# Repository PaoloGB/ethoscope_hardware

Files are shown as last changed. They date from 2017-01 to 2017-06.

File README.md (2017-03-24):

Ethoscope Hardware
========================
This is the hardware repository of the [ethoscope platform](http://gilestrolab.github.io/ethoscope).
It contains 3d printable files and instructions that altogether should be sufficient to build ethoscopes, arenas and modules.

The software repository lives [here](https://github.com/gilestrolab/ethoscope)

Organisation
==================
This repo is organised as follows:
  1. There is a collection of folders for every part in the Ethoscope.
  2. Inside each folder there is a README file explaining the function of the part and how to put it together.
  3. There is also a folder for each sub-part.
  4. Inside each terminal folder you can find the last version of the hardware with a README explaining its function in detail.

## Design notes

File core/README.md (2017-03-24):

Ethoscope core
==============

This document describes the core of the ethoscope device.
The original onshape repository for the core is available [here](https://cad.onshape.com/documents/56ac957ce4b06a92e0ed7352/w/0af5bcd5aa6f698123921d81/e/9491b49b9158a49e2b29f937).
The "core" referes to device without arena or extra modules.
it is made of three mainparts:

* the **head**, which contains the Raspebbery Pi and its camera.
* the **base**, which diffuses light though different types of arenas (read about arenas [here](../arenas/README.md)).
* the **side walls**, which simply connect the head to the base.

An assembled core looks like this:

finished_ethoscope

Building a core
------------------

A list of all components (or BOM) is available [here](./BOM.csv).

So before we start, we should have something like:

overview

In addition, you will need several tools and consumables such as:

* Allen keys
* soldering iron
* super glue
* heat shrink
* solder wire (lead free).

GPIO connector
----------------

In order to power the infrared (IR) light, the General Purpose Input Output (GPIO) of the  Raspberry Pi is connected to the base by a ribbon cable.
We can build a simple connector that looks like that:

GPIO

Here, we have used a **21cm long** 6 way ribbon cable.

Base
-----------------

The base acts as an IR light box.
The idea is to reflect IR light upward so it can go through the arena.

In order to put the light together, a little bit of basic soldering is required:

IR light soldering

In the figure above, the yellow dashed lined indicate where we need to solder.

You can also notice that **heat shrink** have been put around the wires so that we ensure proper insulation.

After is has been soldered, the led strip must be passed **from the outside** to the inside of the light box by the connector hole.
Then, we can stick the light to its support, and glue the support to the side of the base:

base

Head
--------------------
The head is the single most important part of the device.
It is made of a Raspberry Pi, and peripherals, enclosed by pair(lower and upper) of 3d printed parts.

The steps to build the head are the following:

1. Generate a **SD card**  (it contains the operating system and all the software used by the ethoscope).
2. Plug the SD card in the Pi.
3. Place the **camera** on the lower part, and screw from the outside using M2 bolts along with the nylon nuts (sub-picture A, below).
4. Position the **Raspberry Pi** in the lower part, above the camera, and screw it from the outside, with two M3 bolts (sub-picture B, below).
5. Connect the camera, the **GPIO connector** and the wireless dongle to the Pi.
6. In the upper part, there are four holes in the corners. They allow us to close the box with screws. You want to **insert a nut in each slit** under the hole,
7. Now, we can **close the box** (sub-picture C, below) and screw the upper and lower parts together, using four M3 screws.
8. The last thing we want to do is plugging the micro-usb power supply in the Pi.

Head steps

Last bits:
Before you can start working, you will have to **change the focus of the camera**.
I am afraid this has to be done manually. A very good explanation is available here(TODO).

The wireless dongle blinks with blue light to indicate that it transmits data. 
According to your expoerimental setup, you may want to blind the LED (e.g. with black tape) in order to prevent interference with the behaviour of your experimental animals.

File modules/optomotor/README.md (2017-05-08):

Optomotor Module
=========================

The optomotor is an ethoscope module that allows us to deliver both mechanical (tube rotation) and optical (LED) stimuli to fruit flies held in individual glass tubes.

The original onshape repository for the optomotors lives [here](https://cad.onshape.com/documents/3d4348ea20384ce925691583/w/6966f4288591c2cdd19df81a/e/ab72f28500a5d560744ab72b).

The assembled module will look like this:
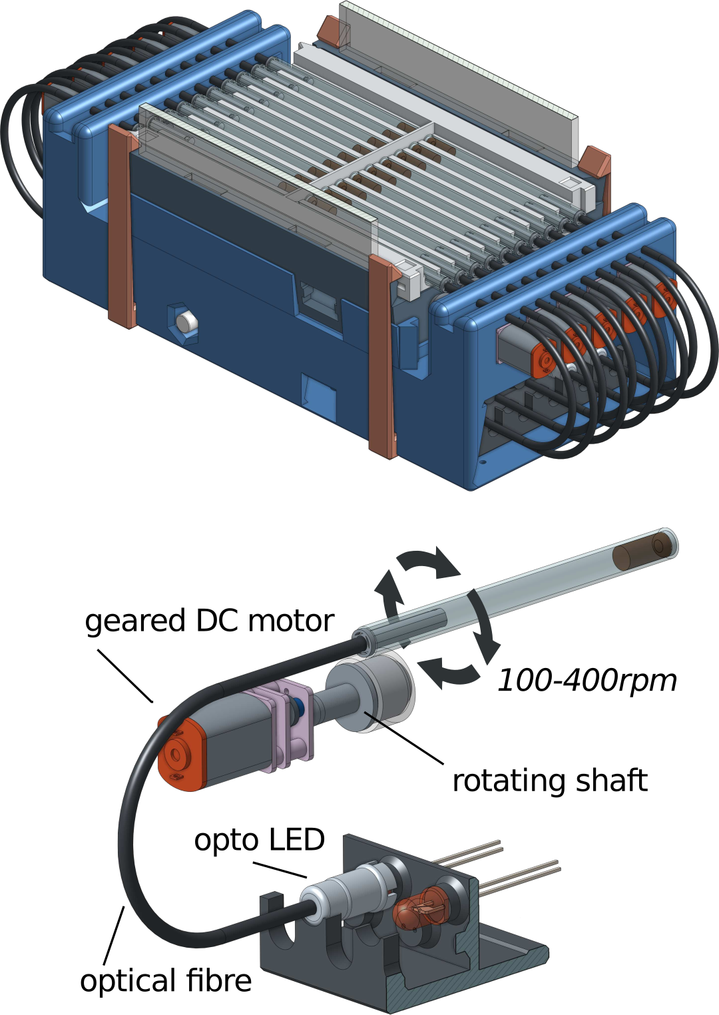
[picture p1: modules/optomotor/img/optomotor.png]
optomotor


Conceptually, the module contains three distinct parts:

* "main", the mandatory components

* "opto", only needed for optical stimulus delivery

* "motor", only needed to rotate tubes

A list of components (BOM) for each part is available [here](BOM.csv).

In this document, we describe how to build both opto and motor parts.

Therefore, before we start, we have something like this:

[[picture overview]]

Main
-----------------------------------------------

The idea is to prepare two electronic boards : [Arduino micro](https://www.arduino.cc/en/Main/ArduinoBoardMicro) and [TLC5943](https://www.adafruit.com/product/1429,15), screw them to the bottom of the main box and connect them to each other.
Also, we add a push button for testing purposes.

###Trimming the main box

The main box is a large print with a lot of support, and it is easier to trim it before putting anything sensitive inside.
Importantly, if you intend to add motors, **ensure you remove all plastic from the cavity that will hold them**.
Indeed, a tiny bit of plastic could end up inside the bear box.

### Arduino board

This is the "master" board that processes input from the computer and coordinate the stimulus delivery.

 1. Solder a 4-pin header (cut a 6-pin header two, 4+2) between pins 3 and 6 (see picture below)

 2. Solder a 2-pin header between pins 11 and 12

 3. Screw the board in place using four 1.2mm diameter screws.

 4. Plug the USB micro cable to the board. Then compile and upload the firmware (you need some degree of familiarity with the Arduino [build process](https://www.arduino.cc/en/Hacking/BuildProcess) for that).
 The code for this firmware lives [here](https://github.com/gilestrolab/ethoscope_hardware/blob/master/modules/optomotor/optomotor.ino).

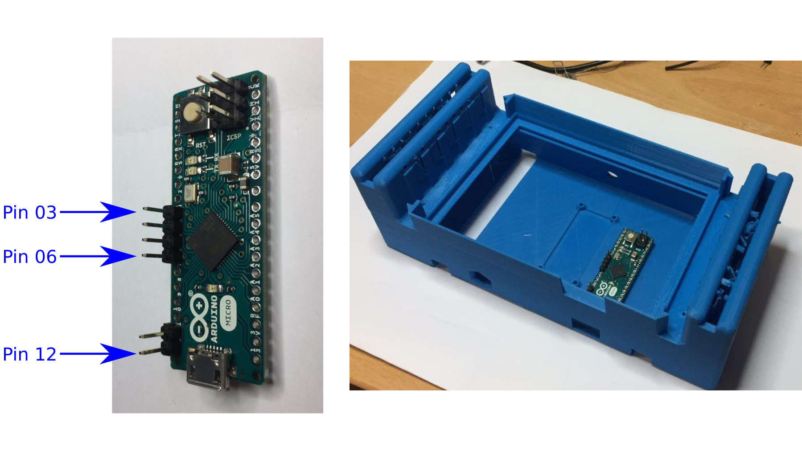
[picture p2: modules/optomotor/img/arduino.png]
arduino


### TLC5943

This board is the "slave".
It is ultimately responsible of turning on/off components (LED/motors).

1. Solder all (i.e. 8) the 6x2 headers (see picture below)

2. Solder the 2 6x1 headers on both extremities of the board

3. Solder the 1.15kΩ resistor

4. Screw the board in place -- using the 2.6mm diameter screws

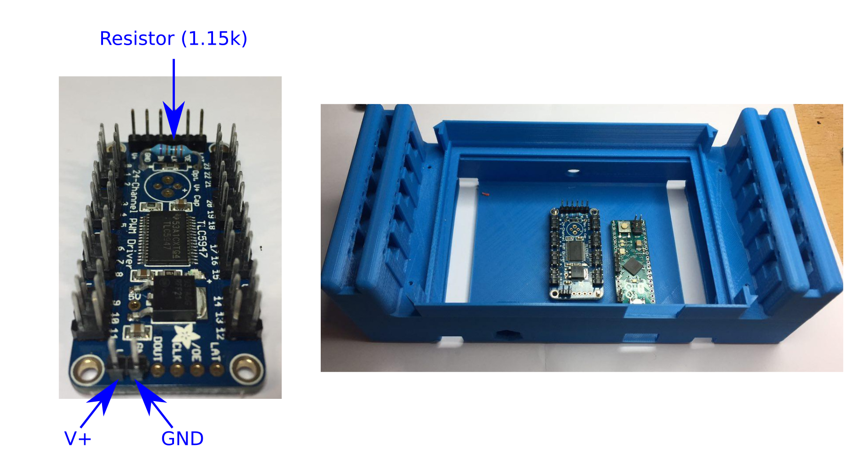
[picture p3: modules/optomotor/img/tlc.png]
tlc


#### Board connector

The connections between the two above boards has to be very robust at all time.

To build the connector (picture below), we use **80mm** of **6-way** ribbon cable. Four of the wires connect the two boards, whilst two bring external power to the TLC5943.

1. Strip all six wires on one end only.

2. Squeeze each wire on a different slot of the 6-way female connector

3. Solder all six wires (this is a bit of a hack, but it works well if you don't have the tool for these connectors)

4. Cut the two wires on the right so that the are only **20mm** long

5. Strip and solder the four remaining wires to the second female connector (the wire must obviously have the same order and position on the second connector -- e.g. in the picture, yellow is on the left of both connectors)

6. Strip the two remaining short wires and add a 2-pin female socket (using two crimps connectors).

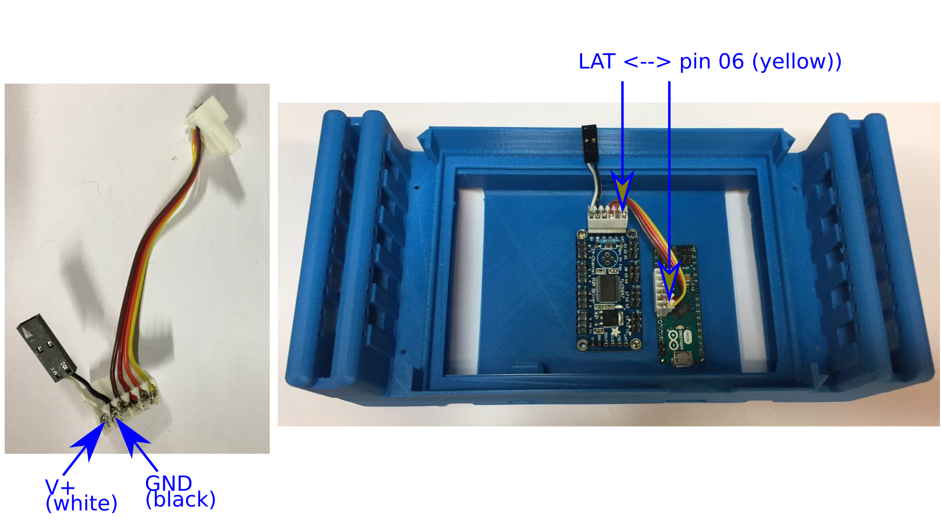
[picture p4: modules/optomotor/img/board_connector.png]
board_connector


###Push button

To assemble the push button:

1. Cut a **150mm**, **3-way** (green, black, white) ribbon cable (picture below)

2. Strip the three wires on one side only, and **preload some heat shrink** before you solder

3. Solder the V+ (white) cable directly to a pin of the push button (it doesn't matter which one)

4. Solder the digital out (green) pin directly to the other pin

5. Solder the ground (black) to the same pin as the digital out, but **through the 1.15kΩ resistor**

6. Retract the heat shrink

7. Cut the ground and V+ wires to **80mm**

8. Use crimps connectors to put ground and V+ in the same 2-pin female socket

9. Use crimps connector to put the digital out wire on a 2-pin female connector (one of the slot will be empty, but do put a crimps connector inside anyway as this makes a better mating between connectors)

10. Bundle all the wires/resistor on the push button end with some larger heat shrink or electrical tape

11. Pass the assembled push button **from the inside of the box to the outside** through the small hexagonal cavity.
Then lock it using the hexagonal screw from the outside.
Admittedly, it is not very easy to spin the push button at this stage, but it will work with some determination!

12. Connect the **V+ and ground pins** to the corresponding pins on the **TLC5943** board

13. Connect the **digital out** wire on **pin 12** of the arduino

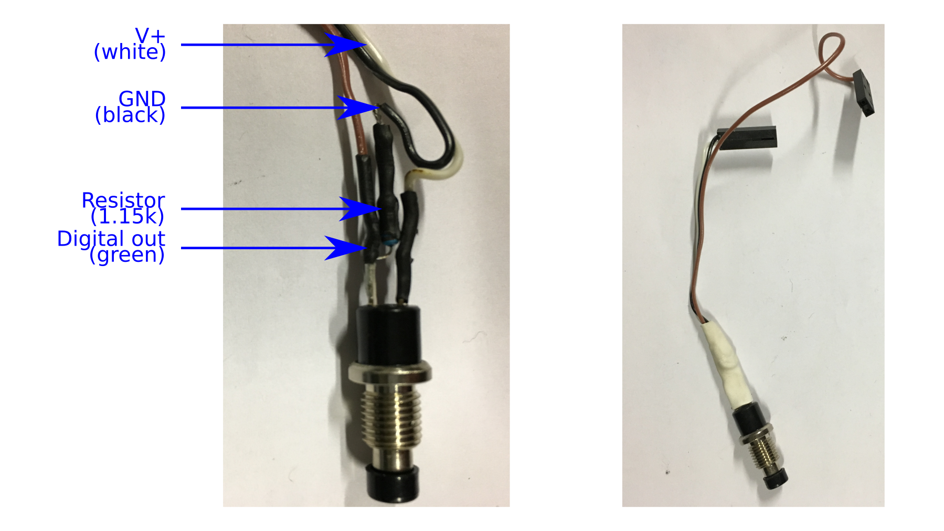
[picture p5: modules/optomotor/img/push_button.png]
push_button


###Power cable

1. Cut the small end of the strip the long USB cable
2. Strip red(V+) and black(GND) cables, cut the others
3. Put some heat shrink around both cables
4. Solder each to a pin of a 2x1 male header
5. Process the heat shrink
6. pass the assembled cable through the circular hole in the back of the box
7. Plug it in the corresponding pins, in the board connector
8. Put a cable tight inside and the outside the box, around the power cable, to prevent stress/disconnection

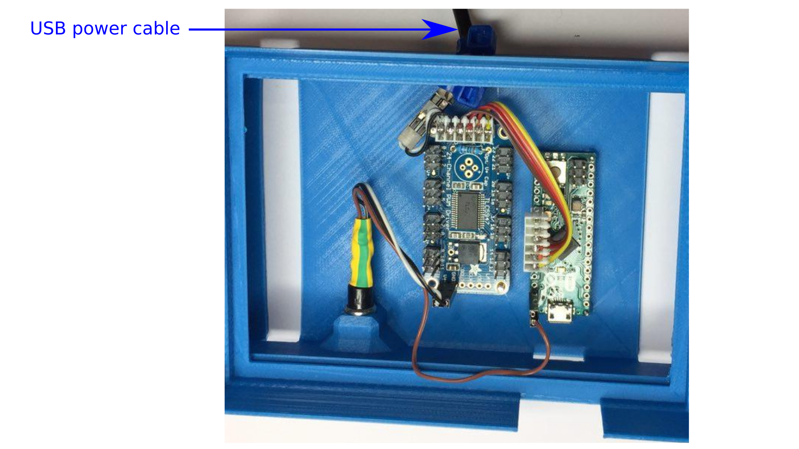
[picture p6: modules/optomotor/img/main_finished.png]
main_finished


Opto
------------------

In order to deliver light to specific tubes, we will make an array of LEDs and connect the LED, with optic fibres, to individual tubes.

Each LED is fitted inside a panel, their are two panels (left and right), each holding five LEDs per machine. The panels are held in position by the "clips"

1. Trim the two panels, so they fit without forcing in the clips.
Also remove any support structure on the LED panels that could have been added by your 3d printer.

2. Set the LEDs so that the **+ side is on the left** (see picture)

3. Cut all the LED legs to 3mm or so

4. Prepare (strip bot ends) as many (10) **75mm**, **2-way** ribbon cables

5. Put a 2-way female socket on one end (using the crimps connectors)

6. Put some heat shrink (5mm should do) on both wires on the other side of the cable.

7. Solder the LEDs. In this document, by **convention**, we use **violet for -** and **light grey for +**

8. Process the heat shrinks

To summarise, this is something like that:

[[picture LED panel]]

Motor
--------------------

Each motor has its own individual slot, so we can just make 10 motors and fit them on the box.
**Ensure you remove all plastic from the motor slots, so that gears don't get stalled**

1. Prepare (strip bot ends) ten **150mm**, **2-way** ribbon cables

2. Put a 2-way female socket on one end (using the crimps connectors)

3. Put some heat shrink (5mm should do) on both wires on the other side of the cable.

4. Solder the motors. In this document, by **convention**, we use **green for -** and **blue for +**.
Each motor will have a small "+" written by the corresponding pole.

5. Pass each motor through its slot in the main box

6. Put its shaft (3d printed small orange part) to each motor

7. Add a ring of silicon (i.e. a section of tube around **5mm long**) to each shaft -- this ensure maximal friction

An assembled motor looks like this:

[[picture assembled motor ]]

Then, when mounted, we have:

[[picture mounted motors]]

Putting things together
-------------------------------------

###Plugging the components to the TLC board.

By convention, **motors are always on even numbers** and **LED, on odd ones**.
In addition, to avoid wires crossing, we map the components the pin facing them, which does not match the numerical order.

So our topology is:

```
MOTOR 01 -> PIN 00  |  PIN 23 <- LED   06
LED   01 -> PIN 01  |  PIN 22 <- MOTOR 06
MOTOR 02 -> PIN 02  |  PIN 21 <- LED   07
LED   02 -> PIN 03  |  PIN 20 <- MOTOR 07
MOTOR 03 -> PIN 04  |  PIN 19 <- LED   08
LED   03 -> PIN 05  |  PIN 18 <- MOTOR 08
MOTOR 04 -> PIN 06  |  PIN 17 <- LED   09
LED   04 -> PIN 07  |  PIN 16 <- MOTOR 09
MOTOR 05 -> PIN 08  |  PIN 17 <- LED   10
LED   05 -> PIN 09  |  PIN 16 <- MOTOR 10
```

## Finishing touches

1. Trim the two clips and fit them on the bottom of the box
2. Lock the clips by sliding the LED panel by the side of the box (if you are not using LEDs, you can simply put panels with no LEDs)
3. Plug both power supply for the TLC and serial connection for the Arduino
4. Press the push button for 5s and release. Check that every component is being activated, in the right order
5. After you have tested the machine, you can decide to mask the various LEDs on both boards if you perform experiments where you don't want any external light
5. Put the roof inside the grove of the box, on top of the boards

[[todo!!]]

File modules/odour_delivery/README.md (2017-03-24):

Odour Delivery Module (ODM) 
=========================
The Odour Delivery Module (ODM) is an Ethoscope module that allows us to delivery up to two different olfactory stimuli to fruit flies held in 14mm glass tubes. 
Odour can be delivered in response to fruitfly behaviour. For instance, following an immobility bout or  a crossing of a virtual midline. 

The ODM can be configured in two different ways; **single** or **dual** odour delivery. 
The frame for dual odour delivery can house two splitters, whereas the frame for single odour delivery houses just one. 
As the former frame is slightly larger, the 3D printed platforms which support the Ethoscope, are slightly different sizes. 
Gcode files for two different versions of the 3D printed frame and platform are available upon request.  
Assembly of the 2 versions of the modules is otherwise similar. 
The assembled odour delivery module with Ethoscope looks like this (this is an example of a a single odour delivery module):

Figure 1 Ethoscope + ODM

A list of components (BOM) for the ODM is available [here](BOM.csv).
In this document we describe how to build the ODM. 
Before we start, this image shows components needed. 
[Pic with all components]
Circuitry
* Cut USB cable 30mm from micro port.  Strip black cable and separate red and black wires inside main cable. Strip black and red cables by approximately 5mm and use micro screwdriver to secure **black cable into VS1-** and the **red into VS1+** on region of lynx motion board labeled 1. 
* Plug in mini port of 2nd USB cable [2].
* Plug in power supply to Anker 40w PSU and USB cable into USB port of computer. **Press the button labeled 3 until green and red lights (labeled 4) are both on and not flashing**. Use a piece of blue tac to cover the lights so they do not disturb the flies during an experiment.
* Place the lynx motion in the base of the frame so that the pins labeled VS1 are in the center.  
* Self-adhesive cable clips can be used to secure the cables and lynx motion into the bottom of the frame (not shown). This can prevent the power supply disconnecting from the lynx motion.

Figure 2 Preparation of Lynx motion
* Next, take the using the 2x10mm screws, secure the 10 x 9G servo motors to the frame of the 2 3D printed shelves (2 screws per servo). 
* Plug the cables of the servo motors into the lynx motion board (Figure 3). The brown cable should correspond to the pin on the outer edge of the VS1 row of pins. The servos should be plugged in the following order:
Servo number
Pin label on lynx motion
1 (shelf 1)
0
2 (shelf 2)
1
3 (shelf 1)
2
4 (shelf 2)
3
5 (shelf 1)
4
6 (shelf 2)
5
7 (shelf 1)
6
8 (shelf 2)
7
9 (shelf 1)
8
10 (shelf 2)
9

* Run script ‘zero_all_servos.py’ to zero all the servos [Q can you update here with link to python script for this part]. 
* Using the 2x6mm screws, screw the cog onto the servos (shortest straight edge of cog should be closest to base of shelf and exactly parallel), whilst they are being locked at 0 position. Make sure that the cogs are tightly secured (these can be printed at 101% to make extremely tight).  
* Insert the Lego Technic Pins. Screw into place using the 2x6mm screws (optional).
 
Figure 3 Servo configuration

Modifying Lego Pneumatic valves
Some of the pneumatic valves are quite stiff and need to be modified; otherwise we find the servos burn out quickly whilst changing lever position during experiments. Please use cut proof gloves and eye protection for this part.
You will need a vice, Stanley knife (with sharp blade), super glue and dust cleaner spray can.
-Place lego pneumatic valve in vice with back edge facing towards you. Using the Stanley knife slice down the grooves between the back panel and valve case. Rotate the valve in vice and cut along the grooves until the glue sticking 3 edges of the back panel to the valve case, is broken.
[Insert pic]
-The back panel is also glued inside the valve to a plastic rod. The dimple in the back of the valve back panel indicates the point of adhesion, so once the back panel is loosened; you will need to slip the knife inside the valve and slice along the back panel to break this glue. To remove the back panel fully you will also need to cut inside parallel to the back panel at two top corners of the valve (see figure?)

[insert pic with cut lines]

- Once the back panel is removed, carefully remove the black lever mechanism. Place somewhere it will not get dusty. It is coated with an oil based lubricant, so be careful not to remove this. 
-Next you will need to remove two small nodules on the inside edge of the valve base. This will allow the black lever mechanism to move more freely from side to side. Do this using the Stanley knife. 
-Clean any shards of plastic from the inside of valve using the dust cleaner spray. Replace the black lever mechanism and stick the back panel back on using a small amount of superglue on each corner. 
-Place in clamp and allow to dry.
-Test valve is working properly and the lever moves freely following this modification. 
Final Steps of Assembly
-Place the 3D printed lever onto the black lever mechanism of the valve (rounded edge down).
- With correct alignment, the two holes in the base of the lego valve should slide onto the lego technic pins (already screwed onto shelves), and the 3D printed lever should slide into the square hole on the 3D printed cog attached to the servo. The lego pneumatic valve should click into place as there is a small lip on the edge of the lego technic pins.
- Next take 1 or 2 fish tank splitters (depending on frame being used) and using a Stanley knife, shorten the length of the input by 15mm. Attach the 10mm OD silicone tubing to the input. Place the 10 or 20 (depending on configuration) 5mmOD12mm lengths of silicone tubing on each of the splitters output. 
[image]
-Thread the 10mm OD silicone tubing through the hole(s) in the 3D printed frame (from inside to out) and slot the fish tank splitter(s) into the groove(s) in the frame. 
-Using the 2x10mm screws, screw the shelves onto the frame,(lego valves facing outwards and servo backs inside). Use sandwich bag wires to tie the servo cables and tuck under the shelves. 
* make sure that servo 1 is to the front left hand side of the ODM Servo 10 should be back right hand corner  (when the hole(s) for the 10mmOD tubing is facing you).
- For single odour delivery, attach the 5mmOD silicone tubing (which is attached to splitter to the lower port of each valve (Figure 4).

Figure 4 Single odour delivery
-For dual odour delivery, attach all 5mmOD silicone tubing originating from one splitter to the upper left port and all of the 5mmOD silicone tubing originating from the second to the upper right port (Figure 5). 

Figure 5 Dual odour delivery
- Using 2x6mm screws attach 3D printed platform to top of frame. There are two Gcode versions of this platform depending on whether you are using frame designed to hold 1 or 2 fish tank splitters (Figure 6). The Ethoscope sits on top of the ODM. Flies within the glass tubing (L,OD,ID: 140mm, 5mm, 3mm) in the Ethoscope arena are connected to the odour supply via 5mm (OD) silicone tubing connecting to the left upper port (for single odour delivery) and the bottom middle port (for dual odour delivery). The USB cable from ODM connects to Ethoscope USB port. Both Ethoscope and ODM connect to power supply. 

Figure 6 ODM with platform

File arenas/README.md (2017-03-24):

Arenas
==================

Arenas are a crucial part of experimental design using the ethoscope platform.
The original onshape repository for all arenas lives [here](https://cad.onshape.com/documents/56ac92e6e4b07682577ddeb3/w/f75f54bb0e265153acfec7dd/e/395a5571e38d50273e8a240c).

An arena is physical translation of an experimental paradigm.

With the ethoscope platform, it is possible to work with multiple arenas according to your biological question and model organism.

Arenas are generally 3d printed and can be derived from templates.
Template arena have the suffix **"template"**

There are several conventional sizes of arena that corresponds to the camera mode of the ethoscopes.
namely, the sizes:

* standard 
* *mini* (the keyword mini is in the name of these arenas)

The mini arenas have smaller surfaces and are optimises for HD video acquisition.
The standard size is a good compromise between image surface and time resolution allowing users to perform real time tracking

Adding new arenas
--------------------------

When adding new arena. Please, provide:

* A README with a description (and and name, author, number of rois,...)
* An stl file
* A 1min mp4 video of the arena with animals. It can be done with `ffmpeg` (e.g. `ffmpeg -ss 00:01:00 -i input.mp4  -t 00:01:00  -c:v libx264 -preset veryslow -crf 26  arena_xxx_xxx.mp4`)

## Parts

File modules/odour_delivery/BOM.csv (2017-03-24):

Piece | Part | Quantity | Supplier | Reference
Frame- 2 versions available | Main | 1 | 3D printed | Gcode file available on Gglab Onshape
Shelves | Main | 2 | 3D printed | Gcode file available on Gglab Onshape
Cogs | Main | 10 | 3D printed | Gcode file available on Gglab Onshape
Levers | Main | 10 | 3D printed | Gcode file available on Gglab Onshape
Platform- 2 sizes available | Main | 1 | 3D printed | Gcode file available on Gglab Onshape
LEGO Pneumatic Two-way Valve with Pinholes (47223) | Main | 10 | Brickowl | http://www.brickowl.com/catalog/lego-pneumatic-two-way-valve-with-pinholes-47223
LEGO Technic Pin with Lengthwise Friction Ridges and Center Slots (2780 | Main | 20 | Brickowl | http://www.brickowl.com/catalog/lego-technic-pin-with-lengthwise-friction-ridges-and-center-slots-2780
2x6mm screw | Cog screw | 10 | Amazon | http://www.amazon.co.uk/Tapping-Thread-Round-Phillips-Screw/dp/B00GMQDSRI
2x 10mm screw | Servo, shelf and platform screws | 28 | Amazon | http://www.amazon.co.uk/dp/B00MFBTWMO/ref=pe_385721_37986871_TE_item
9G microservos 4.8V | Circuitry | 10 | roboscop | http://www.robotshop.com/uk/9g-micro-servo-motor-4-8v.html
Lynx Motion SSC-32 Servo Controller | Circuitry | 1 | Roboshop | http://robotshop.com/en/lynxmotion-ssc-32-servo-controller.html
USB A to micro cable | Circuitry | 1 | RS | RS 888-8811
USB A to mini cable (30cm) | Circuitry | 1 | Amazon | http://www.amazon.com/30CM-male-plug-leads-Cable/dp/B00MMVLH9I
10 Way Fish Tank Splitters | odour delivery | 1 o 2 depending on setup | Ebay | http://www.ebay.co.uk/itm/281812927693
Sillicone tubing OD, ID, WT (5mm,3mm,1mm) | odour delivery | 20 x 12mm lengths | VWR
Sillicone tubing OD, ID, WT (10mm,6mm,2mm) | odour delivery | 1 or 2 x 300mm (depending on setup) | VWR
Anker 40w PSU | Power supply | 1 | Amazon | ?

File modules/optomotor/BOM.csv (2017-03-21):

Piece | Part | Quantity | Supplier | Reference | Price(approx., in $) | Stock
Main box | main | 1 | Polygonal Tree/Custom made | TODO | 0
Box clips | main | 2 | Polygonal Tree/Custom made | TODO | 0
Shafts | main | 10 | Polygonal Tree/Custom made | TODO | 0
LED Panels | main | 2 | Polygonal Tree/Custom made | TODO | 0
Circuit roof | main | 1 | Polygonal Tree/Custom made | TODO
USB A to micro cable(50cm) | main | 1 | Farnell | http://uk.farnell.com/multicomp/mc001008/usb2-0-a-male-to-micro-usb-b-m/dp/2506103 | 3
USB A (Power supply) | main | 1 | RS | http://uk.rs-online.com/web/p/products/8888811
Screws (M2.6 x 8mm) | main | 2 | RS | http://uk.rs-online.com/web/p/products/6644956/
Screws (M1.2 x 6mm ) | main | 2 | RS | http://uk.rs-online.com/web/p/products/4187218/
Arduino micro | circuitry | 1 | RS | http://uk.rs-online.com/web/p/products/7798864 | 15
TLC5947 PWM Driver | circuitry | 1 | Adafruit | https://www.adafruit.com/product/1429 | 15
Push button | circuitry | 1 | RS | http://uk.rs-online.com/web/p/products/1336502 | 2.5
PCB Headers (2 x 3) | circuitry | 8 | RS | http://uk.rs-online.com/web/p/pcb-headers/2518137 | 0.2
Right angle 6 way socket | circuitry | 3 | RS | http://uk.rs-online.com/web/p/idc-connectors/5437750/ | 0.3
PCB Header (1 x 6) | circuitry | 3 | RS | http://uk.rs-online.com/web/p/pcb-headers/6812994/ | 0.4
Female 2 pins crimps | circuitry | 20 | Farnell | http://uk.farnell.com/multicomp/2226tg/crimp-terminal-24-28awg/dp/1593506 | 0.24
Crimps contact | circuitry | 40 | Farnell | http://uk.farnell.com/multicomp/2226tg/crimp-terminal-24-28awg/dp/1593529 | 0.06
Ribbon cable | circuitry |  | RS |  | 0
Resistor (1.15k) | circuitry | 2 | RS | http://uk.rs-online.com/web/p/through-hole-fixed-resistors/7548691/ | 0.25
N20 gear motor | motor | 10 | ??? | ??? | 4
Silicon tubing 6x9 mm | motor | 1 | VWR |  | 2
Filter Box | opto | 1 | Polygonal Tree/Custom made | TODO | 0
IR filters | opto | 1 | TODO | TODO | ?
Light Guides (8in) | opto | 5 | RS | http://uk.rs-online.com/web/p/led-light-pipes/8905782 | 2.5
LED Fibre Optic Couplers | opto | 10 | Mouser | http://www.mouser.co.uk/ProductDetail/VCC/THR_5_22/ | 0.6
630 nm LEDs | opto | 10 | RS | http://uk.rs-online.com/web/p/visible-leds/9047367 | 0.15

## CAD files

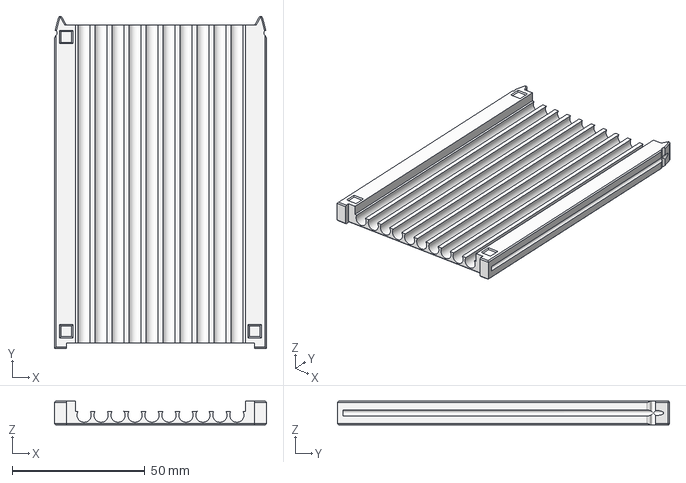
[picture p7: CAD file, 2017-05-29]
arenas/arena_10x1_longTubes/arena_10x1_longTubes.step
80.0 x 125.2 x 9.00 mm

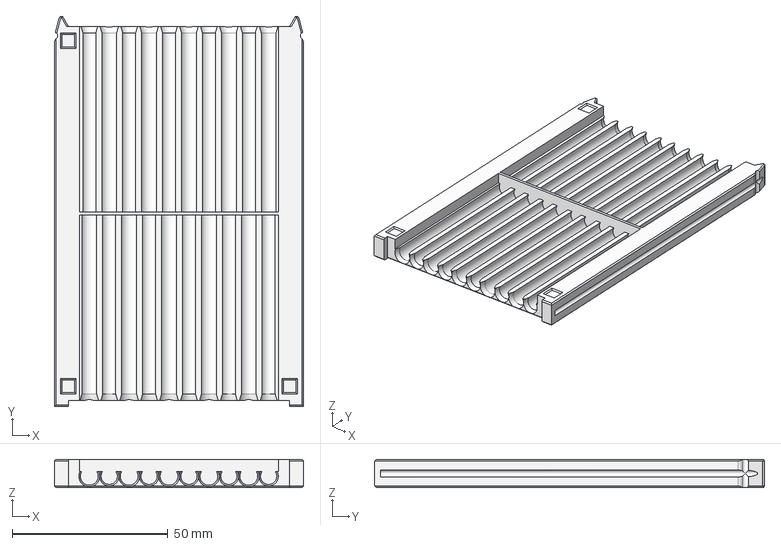
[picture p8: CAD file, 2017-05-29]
arenas/arena_10x2_shortTubes/arena_sdModule.step
80.0 x 125.2 x 9.00 mm

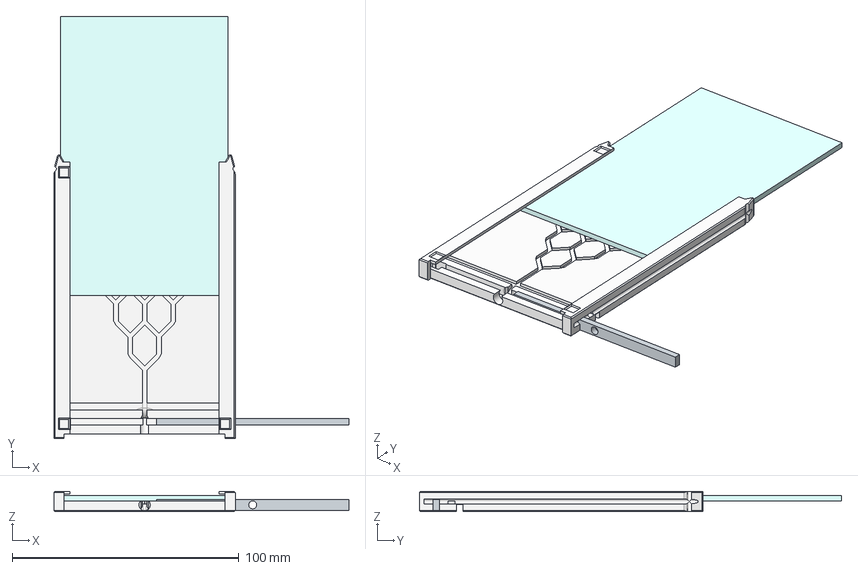
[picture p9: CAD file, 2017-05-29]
arenas/arena_gauss/Gauss.step
130.2 x 186.3 x 9.00 mm
arena_binary_tree
Glass_lid
slider

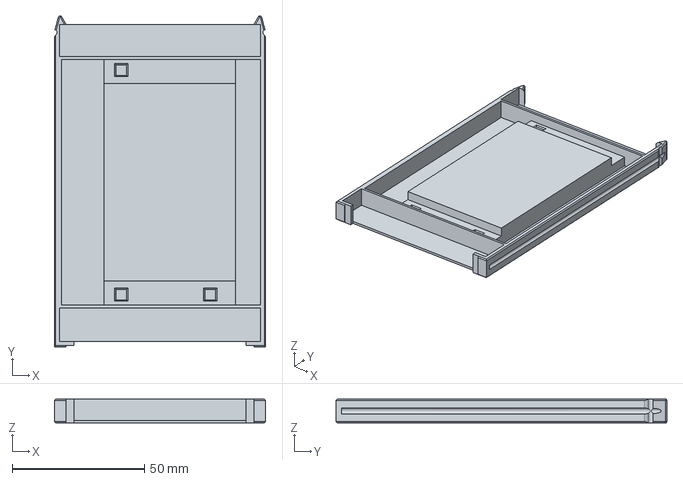
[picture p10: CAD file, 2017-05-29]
arenas/arena_mini_template/arena_mini_template.step
80.0 x 125.2 x 9.00 mm

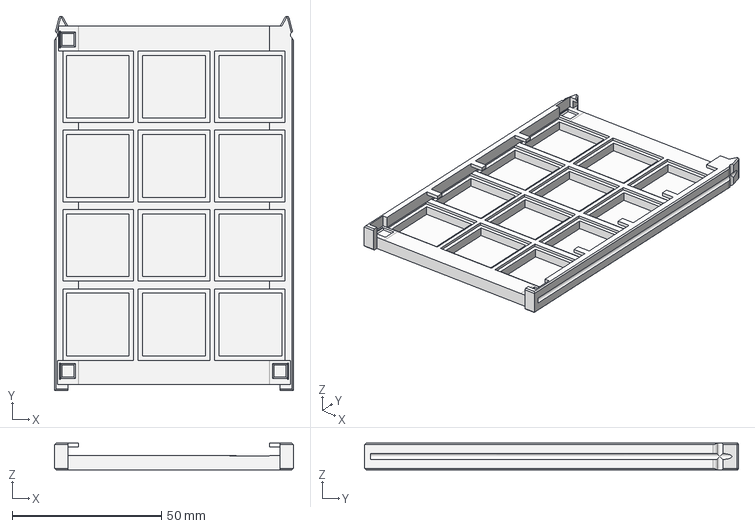
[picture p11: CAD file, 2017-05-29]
arenas/arena_squares/arena_squares.step
80.0 x 125.2 x 9.00 mm

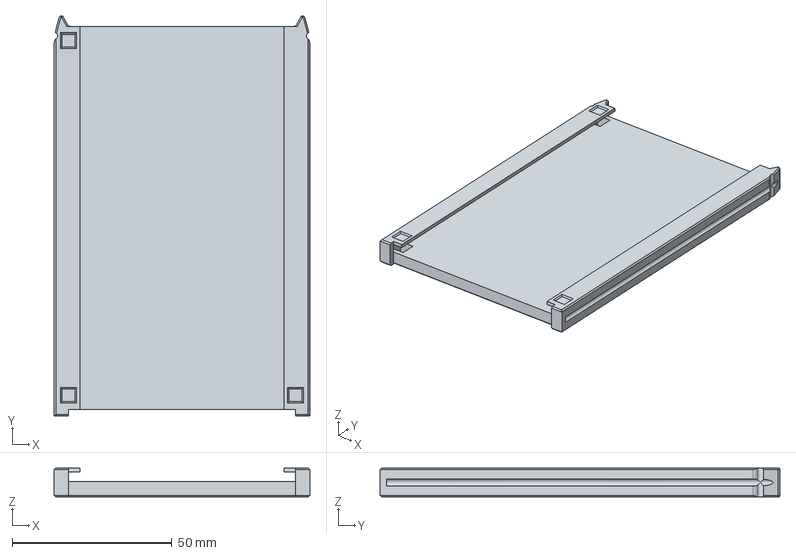
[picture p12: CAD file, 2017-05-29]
arenas/arena_template/arena_glassLid_template.step
80.0 x 125.2 x 9.00 mm

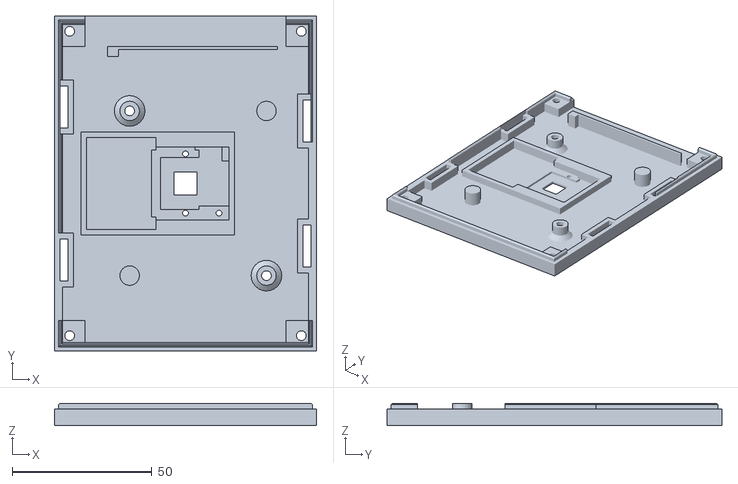
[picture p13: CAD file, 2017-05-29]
core/lower_pi_case/lowerPiCase.stl
94.0 x 120.0 x 8.00

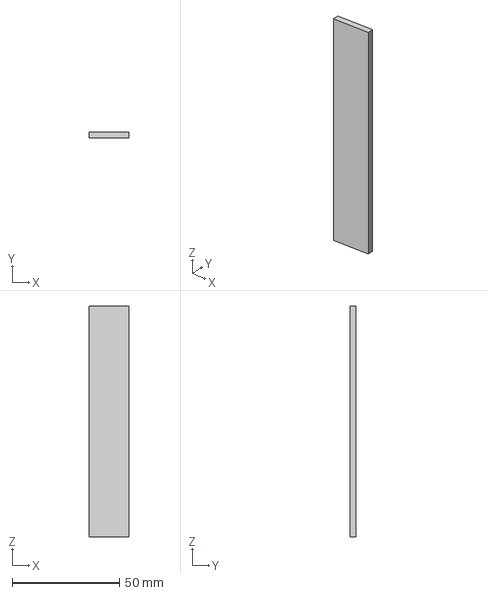
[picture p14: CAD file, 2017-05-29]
core/side_wall/LightTile.step
18.7 x 3.00 x 107.7 mm

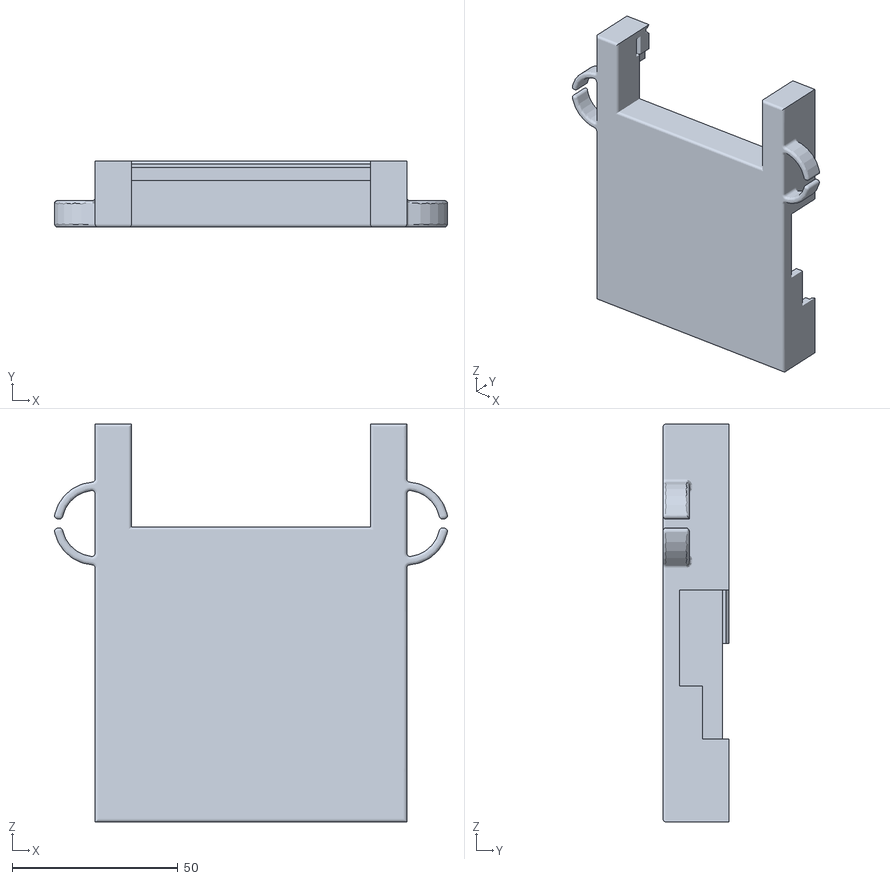
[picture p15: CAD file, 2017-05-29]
core/upper_pi_case/upperPiCase.stl
118.5 x 20.0 x 120.0

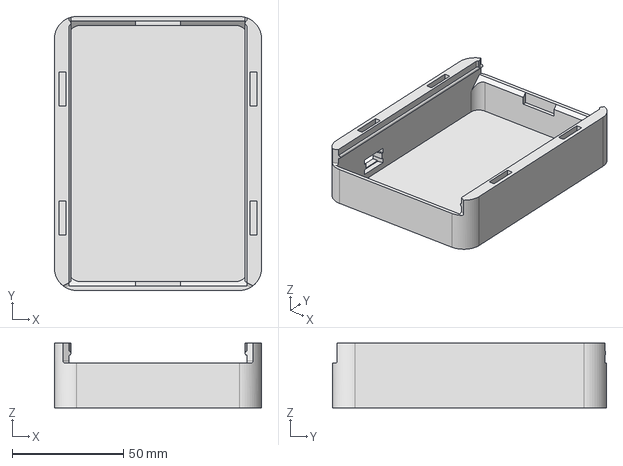
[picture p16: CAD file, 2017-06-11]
core_Rymapt/LightBox/core_lightBox_R2.stp
93.0 x 123.0 x 29.0 mm

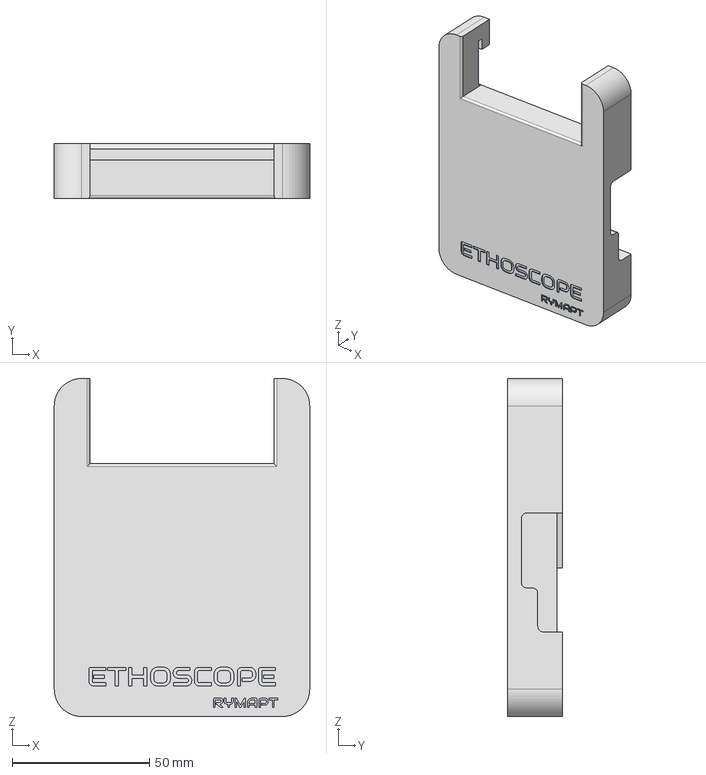
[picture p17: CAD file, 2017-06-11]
core_Rymapt/PiCase/upperPiCase_R2.stp
93.0 x 20.0 x 123.0 mm

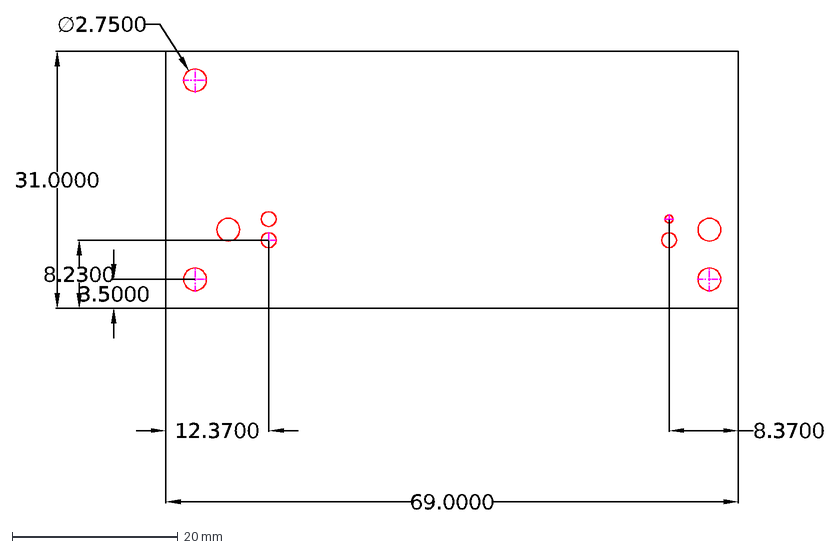
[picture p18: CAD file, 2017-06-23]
core_Rymapt/Shield/ShieldBare.dxf
69.0000
31.0000
∅2.7500
12.3700
8.3700
8.2300
3.5000

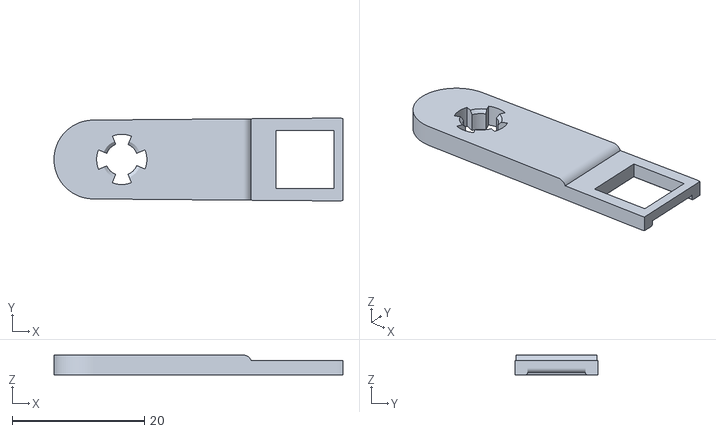
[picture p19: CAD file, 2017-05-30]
extra/Spanner/RPi_Lens_Spanner.5.stl
43.8 x 12.6 x 3.00

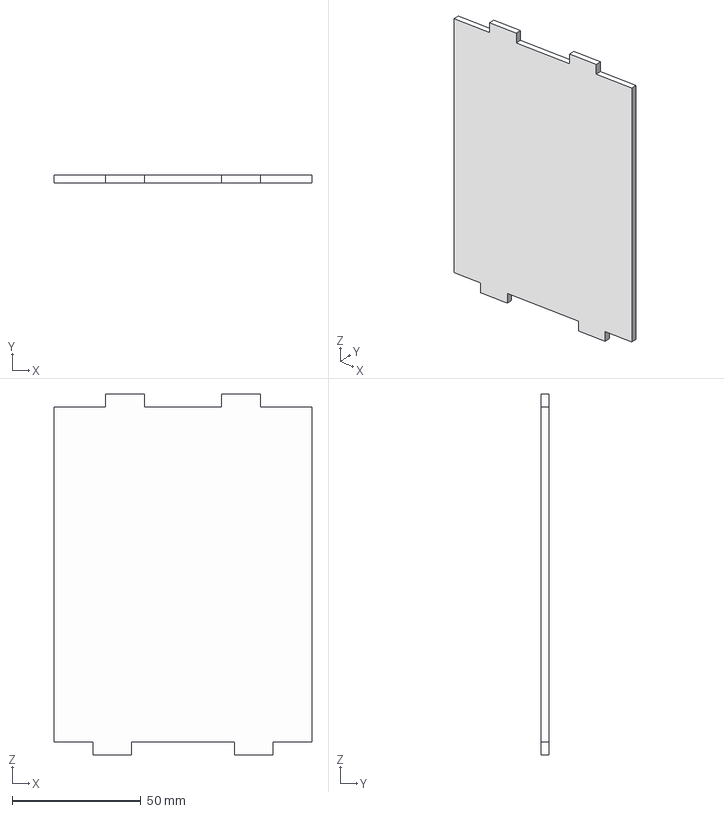
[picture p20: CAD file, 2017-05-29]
core/side_wall/core_laterals - Wall - Small.step
100.0 x 3.00 x 140.0 mm

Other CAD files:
core_Rymapt/LightBox/sideWall_R2.dxf
core_Rymapt/PiCase/lowerPiCase_R.stl
extra/Spanner/RPi_Camera_Lens_Socket_wrench.6.stl
Assembled.iam
Assembled/AIP/Cable and Harness/Assembled.Harness1.iam
Assembled/AIP/Cable and Harness/Assembled.Harness1.ipt
arenas/arena_10x1_longTubes/arena_10x1_longTubes.ipt
core/RPi3/OldVersions/RasPi_Camera.0001.ipt
core/RPi3/RasPi_Camera.ipt
core/light_box/core_lightBox.ipt
core/lower_pi_case/OldVersions/lowerPiCase.0001.ipt
core/lower_pi_case/lowerPiCase.ipt
core/side_wall/LIghtTile_new.ipt
core/side_wall/LightTile.ipt
core/side_wall/OldVersions/LIghtTile_new.0001.ipt
core/side_wall/OldVersions/SideWall_new.0002.ipt
core/side_wall/OldVersions/SideWall_new.0003.ipt
core/side_wall/SideWall.ipt
core/side_wall/SideWall.step
core/side_wall/SideWall_new.ipt
core/side_wall/core_laterals - Wall - Small.ipt
core/upper_pi_case/OldVersions/upperPiCase_new.0001.ipt
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

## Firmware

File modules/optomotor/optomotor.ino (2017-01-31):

/* Program using Adafruit TLC5947 to control up to 24 components with pwm.
 *  Usage:
 *  
 * P CHANNEL DURATION(ms) [INTENSITY](0-1000)
 * 
 * CHANNEL is a componenet from 0 to 23.
 * DURATION defines how long this compoenet is to be activated for (in ms)
 * INTENSITY is the duty cycle of the PWM  (optional, from 0 to 1000)
 * 
 * example:
 * P 2 1000
 * P 0 1000 500
*/


#include <SoftwareSerial.h> 
#include <SerialCommand.h>
#include <Adafruit_TLC5947.h>


#define BAUD 115200
#define N_OUTPUTS 24

// a set of timers measuring how long a given output should remain on for
int timers[N_OUTPUTS] = {0};
// stores the PWM of each output
unsigned int pwms[N_OUTPUTS];

unsigned long t0 = 0;
unsigned long t1 = 0;

SerialCommand SCmd;

/* ======================== TLC 5947 ======================== */
#define NUM_TLC5974 1

#define MAX_PWM 4095   
#define MIN_PWM 0   

// Define Pinouts from Arduino to SPI pins on LED Driver Board
#define TLC_DATA_PIN 3
#define TLC_CLOCK_PIN 4
#define TLC_LATCH_PIN   6
//#define oe  -1  // set to -1 to not use the enable pin (its optional)

Adafruit_TLC5947 tlc = Adafruit_TLC5947(NUM_TLC5974, 
                                        TLC_CLOCK_PIN,
                                        TLC_DATA_PIN,
                                        TLC_LATCH_PIN);

/* ======================== Push button======================== */

#define PUSH_BUTTON_PIN 12
// how long (in ms) the push buton should be hold for before demo is run
#define PUSH_BUTTON_THR 2000
// a timer that records how long push button is pressed for
int push_button_timer = 0; 




void setup() {
  Serial.begin(BAUD);
  SCmd.addCommand("P",sendPWMSerial);  
  SCmd.addCommand("D",demo);  
  SCmd.addCommand("H",help);
  //SCmd.setDefaultHandler(help);  
  
  tlc.begin();
  
  for (unsigned int i = 0; i != N_OUTPUTS; ++i){
    pwms[i] = 0;
    timers[i] = 0;
    tlc.setPWM(i,0);
  }
  tlc.write();

  pinMode(PUSH_BUTTON_PIN, INPUT);
}

void help(){
  Serial.println("P CHANNEL DURATION(ms) [INTENSITY](0-1000)");
  }
void loop() { 
  SCmd.readSerial(); 
  delay(50);
  t0 = t1;
  t1 = millis();
  
  //fixme overflow of time!
  // i.e. if t0 > t1
  unsigned int tick =  t1 - t0;

  for (unsigned int i = 0; i != N_OUTPUTS; ++i){
    if(timers[i] != 0){
       timers[i] -= tick;
       if(timers[i] <0){
        timers[i] = 0;
        tlc.setPWM(i,MIN_PWM);
        tlc.write();
      }
    }
  }
  if(digitalRead(PUSH_BUTTON_PIN) == LOW){
    if(push_button_timer > PUSH_BUTTON_THR)
        demo();
    push_button_timer = 0;
  }
    
  else{
    push_button_timer += tick;
      
  }
}


void sendPWM(unsigned int idx, unsigned int duration, unsigned int duty_cycle = MAX_PWM){
  timers[idx] = duration; // in ms
  tlc.setPWM(idx,duty_cycle);
  tlc.write();
}

void demo(){
  Serial.println("DEMO");
  for (unsigned int i = 0; i != N_OUTPUTS; ++i){
    tlc.setPWM(i,MAX_PWM);
    tlc.write();
    delay(500);
    tlc.setPWM(i,MIN_PWM);
    tlc.write();
  }
}

void sendPWMSerial(){
  char *arg;
  arg = SCmd.next();  
  unsigned int motor_id = 0;
  unsigned int duration = 0;
  unsigned int duty_cycle = MAX_PWM;
  unsigned int power = 0;
  
  if (arg != NULL) 
    motor_id = atoi(arg) ;
  else
   return; 
   
  arg = SCmd.next();   
  if (arg != NULL)
    duration = atoi(arg) ;
  else
    return;
  
  arg = SCmd.next();   
  if (arg != NULL){
    power = atoi(arg);
    duty_cycle = ((uint32_t)  power * (uint32_t) MAX_PWM)/1000;;
  }
  sendPWM(motor_id, duration, duty_cycle);
  }

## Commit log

2016-12-05 rename project
    [BOM.csv]
2016-12-05 BOM ++
    [BOM.csv]
2016-12-07 add filters to bom. please fill the rest
    [BOM.csv]
2017-01-18 added screws and power to BOM
    [BOM.csv]
2017-01-31 update doc
    [BOM.csv]
2017-05-29 First commit, changed a few things, add a RYMAPT folder with newly shaped Ethoscope
    [Assembled.0003.ipn, Assembled.Harness1.iam, Assembled.Harness1.ipt, Assembled.iam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]
2017-05-30 Edited the uppercase. It should now be ok
    [Assembly_Rymapt_Ethoscope.iam, M2_nut.ipt, M2_phillip_8mm.ipt, M3_hex_12mm.ipt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]
2017-06-02 Modified screw sizes to use only M2 and M2.5 everywhere
    [Assembly_Rymapt_Ethoscope.iam, lowerPiCase_R.ipt, lowerPiCase_new.ipt, upperPiCase_R.ipt]
2017-06-02 Added side walls, modified base to make slot at least 3 mm wide. Still a few issues with alignment.
    [Assembly_Rymapt_Ethoscope.iam, core_lightBox_R.ipt, lowerPiCase_R.ipt, sideWall_R.ipt]
2017-06-08 R2 now have equally spaced wall inserts
    [Assembly_Rymapt_Ethoscope.0004.iam, Assembly_Rymapt_Ethoscope2.iam, LightStrip_R.dxf, core_lightBox_R.stl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]
2017-06-11 Removed clips. Tweaked microUSB slot.
    [Assembly_Rymapt_Ethoscope2.iam, upperPiCase_R.ipt, upperPiCase_R2.ipt]
2017-06-11 Stl files
    [core_lightBox_R2.stl, core_lightBox_R2.stp, lowerPiCase_R2.stl, upperPiCase_R2.stl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]
2017-06-22 Shield design
    [ShieldAssembly.0001.iam, ShieldAssembly.iam, ShieldBare.0002.ipt, ShieldBare.dwg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]
